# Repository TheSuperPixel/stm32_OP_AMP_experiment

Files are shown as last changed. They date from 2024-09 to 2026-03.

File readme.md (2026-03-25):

# stm32运放实验演示电路
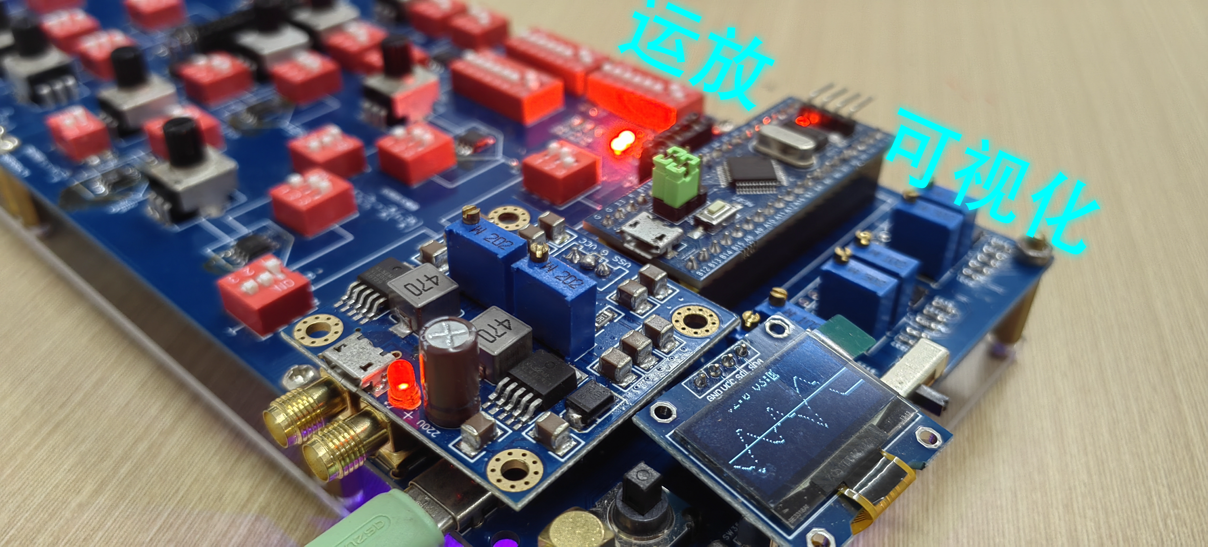
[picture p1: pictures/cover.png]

## 简介
这是stm32运放实验演示电路，我把许多常用运放电路集成到了一个板子上，通过拨码开关来改变不同电阻大小挡位，通过转动旋钮可调节输入电压大小。然后使用运放前级处理电路，把电压映射到0-3.3V，用stm32读取电压信息，通过线性运算算出原本电压，并显示到oled上，能通过OLED显示内容直观了解和学习运放的输入输出电压关系。因为电路设计，运放精度偏差，ADC调理电路和电源质量限制,实际上OLED显示的内容和公式有一定偏差,但是大致关系是正确的。这个电路仅用于演示运放能用于计算的特性，不用于实际的信号处理。
## 演示视频
https://www.bilibili.com/video/BV1tPsaeoEXa
## 硬件组装调试说明
### 1.PCB打板
pcb文件位于 **./pcb** 文件夹下，内有5张pcb文件，Board1是最终版本电路的左边部分，Board2是最终版本电路的中间部分，Board4是最终版本电路的右边部分，其余两张电路板，也就是Board3和Board_all，是上一版本的文件，在最新版运放实验演示电路中，已经不需要了，最后只需打板Board1，Board2和Board4即可。
### 2.Board1焊接制作
Board1的所有运放芯片需要焊接**LM358**或引脚定义相同的运放，不能按照原本的电路图焊接LM393，旋转电位器旋钮建议使用1K以上的阻值，否则会因为电流过大造成发热和过载。其余元件按照原理图设计焊接即可。
### 3.Board2焊接制作
Board2的所有运放芯片需要焊接**LM358**或引脚定义相同的运放，不能按照原本的电路图焊接LM393；**R127**,**R129**和**R131**使用0欧电阻焊接，**R128**,**R130**和**R132**不焊接。旋转电位器旋钮建议使用1K以上的阻值，否则会因为电流过大造成发热和过载。其余元件按照原理图设计焊接即可。
### 4.Board4焊接制作
1.Board4左上角**U23**焊接排母；左下方**H4**和**H5**焊接排母，并按照视频内容正确插入与视频对应型号的正负双电源供电板。输出电压调整到**正负10V**。
2.给Board4通电，然后往Board4边缘的IN0连接直流电源。调整Board4右边运放前级处理电路的六个电位器进行校准，使得当IN0输入-10V到10V电压时，运放前级处理电路能把电压映射到0-3.3V。按照这个方法校准IN1和IN2的前级处理电路的电位器。最后，给Board4左上角**U23**按照视频内容正确插入与视频对应型号的stm32f103c8t6最小系统板。
3.把Board4的**sw33**，**sw34**和**sw35**拨到最下面，然后再次给Board4通电，通过控制五向开关，进入菜单的设置页面，调整k1,b1,k2,b2,k3,b3，使得当IN0，IN1，IN2输入-10V到10V电压时，stm32能够显示出和输入电压一样的数值。
### 5.整机调试
使用激光切割机切割出 **./3D模型/底板打印.DWG**形状的文件，厚度选择为3mm。然后，使用铜柱和螺丝，把焊接好的Board1，Board2和Board4依次从左往右安装，把板子摆到水平方向，两块相邻的pcb边缘的排针使用跳线帽横向进行连接。
## 使用方法
开机后，使用五向开关控制菜单进入**start**页面，可以直观查看输入电压，输出电压和对应的电压波形。通过转动旋钮可调节输入电压大小，通过拨码开关来改变不同电阻大小挡位。Board2的**sw28**、**sw29**和**sw30**用于控制不同运放输入输出电路和stm32电压测量的连接关系。如果**sw28**、**sw29**和**sw30**都只有1所在的那位拨到开启状态，则stm32测量的是反相比例器的输入和输出电压；如果**sw28**、**sw29**和**sw30**都只有2所在的那位拨到开启状态，则stm32测量的是同相比例器的输入和输出电压。更多拨码含义见下表：
```
1：反相比例器
2：同相比例器
3：同相加法器
4：反相加法器
5：减法器
6：仪用放大器
7：积分器
8：微分器
```
## 参考资料和其他
1.stm32代码部分主要参考了江协科技的ADC多通道输入实验<br>
https://www.bilibili.com/video/BV1th411z7sn<br>
2.由于ADC前级调理电路设计缺陷，在电路刚上电时，ADC前级调理电路的输出会有超出0-3.3V以外的冲击电压，会影响stm32正常工作，因此，建议在通电前先把stm32取下，通电一段时间后再插回stm32。断电时同理。<br>
3.电路的大部分设计(包含仿真)是2023年大二上刚学习模电的时候做的，难免会有不足之处，请大家见谅。

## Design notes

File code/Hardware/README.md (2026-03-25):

# Third-Party Source Notice (第三方代码声明)

## 来源说明
本目录下的OLED相关代码由 **江协科技** 提供。<br>
本目录下的EEPROM相关代码来自 **蓝桥杯嵌入式赛道EEPROM模板**。

## 版权与协议
* **版权归属：** 版权归原作者所有。

## 免责声明
本项目作者 (TheSuperPixel) 不对引用的代码质量、稳定性或潜在侵权风险负责。

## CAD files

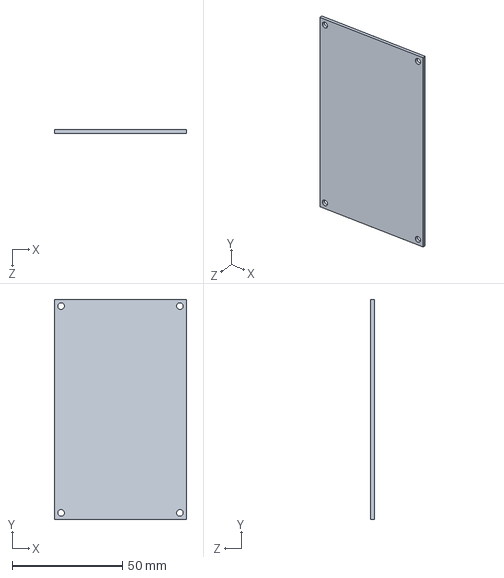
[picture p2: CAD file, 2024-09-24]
3D模型/10_6电路板.SLDPRT
60.0 x 100.0 x 1.60 mm

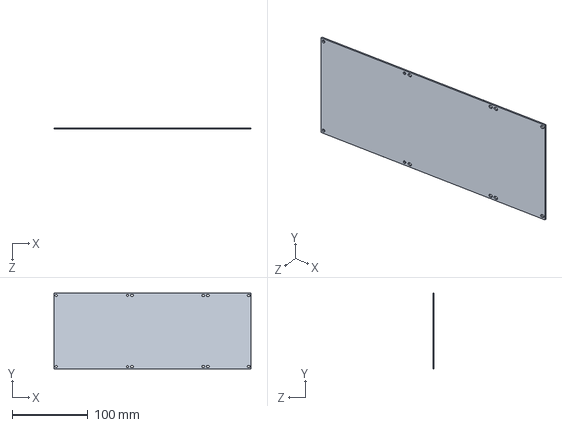
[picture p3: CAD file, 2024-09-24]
3D模型/底板.SLDPRT
260.0 x 100.0 x 1.60 mm

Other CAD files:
3D模型/底板打印.DWG
